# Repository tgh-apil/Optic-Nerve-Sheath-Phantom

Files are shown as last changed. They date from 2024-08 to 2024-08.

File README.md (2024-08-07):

# Optic-Nerve-Sheath-Phantom
A transorbital ultrasonographic optic nerve sheath training phantom based on a model designed by Dr. Zakir Hajat, Dr. Michael Dinsmore, and Dr. Lashmi Venkatraghavan.

This model is based on the pre-existing transorbital ultrasonographic optic nerve sheath phantom described in a [2020 paper by Hajat et al.](https://doi.org/10.1097/ana.0000000000000592), and was developed alongside Dr. Michael Dinsmore for the dual purposes of improving the realism of the training phantom by providing a human face-shaped case in which to house the inner components of the phantom (i.e. the eye and optic nerve sheath) and of increasing its longevity by replacing the gelatine and psyllium fiber with ballistics gel. It also replaces difficult to access components (namely the pediatric microcuffed endotracheal tube) with silicone components that are relatively easy to manufacture. This phantom is intended for training in the measurement of optic nerve sheath diameter through noninvasive ultrasonography.

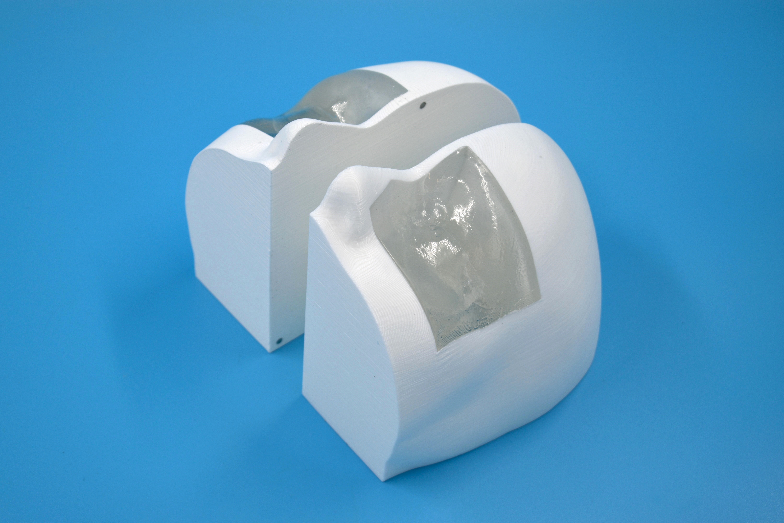
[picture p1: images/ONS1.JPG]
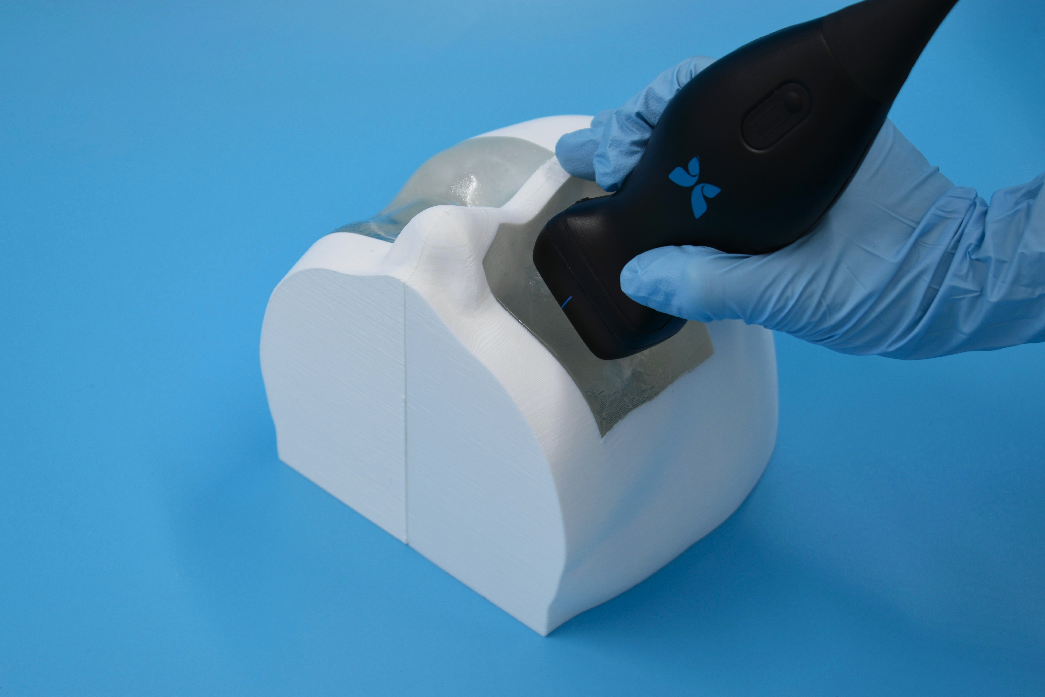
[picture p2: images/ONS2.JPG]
  

Note: The headform model was modified from NIOSH National Personal Protective Technology Laboratory (NPPTL)’s medium size ISO Digital Headform: https://www.cdc.gov/niosh/npptl/topics/respirators/headforms/default.html

This model was developed at the Lynn & Arnold Irwin Advanced Perioperative Imaging Lab, Toronto General Hospital, University Health Network.

## Parts, Materials & Equipment
### Printed Parts List
The files for these parts can be found in the [*/stl files/*](stl%20files) directory.

*/stl files/intermediate molds/* — for silicone casting of intermediate mold
* ONSl_intmold_1.stl
* ONSl_intmold_2.stl
* ONSr_intmold_1.stl
* ONSr_intmold_2.stl

*/stl files/sheath molds/* — for silicone casting of nerve sheath
* ONS_sheathmold_4_5mm_1.stl
* ONS_sheathmold_4_5mm_2.stl
* ONS_sheathmold_5_5mm_1.stl
* ONS_sheathmold_5_5mm_2.stl
* ONS_sheathmold_6_5mm_1.stl
* ONS_sheathmold_6_5mm_2.stl

*/stl files/case/* — for housing eye and nerve sheath in ballistics gel
* ONSl_case.stl
* ONSr_case.stl

*/stl files/other/* 
* ONS_ramp.stl

### Hardware
* 8 x M4 8mm screws
* Table tennis balls (40mm in diameter)
* Super glue
* Magnets (3mm OD), 6 per head (i.e. 3 per half head)

### Printing
* PLA (polylactic acid) filament
* Fused Deposition Modelling 3D printer

### Casting
* [Smooth-On’s Mold Star 20T Silicone Rubber](https://www.smooth-on.com/products/mold-star-20t/) (or another silicone of similar hardness) 
* Hot glue gun
* 5mL syringe
* [Clear Ballistics - 10% Ballistics Gel](https://www.clearballistics.com/product/10-ballistics-gel)
* [Humimic Medical - Medical Ballistics Gel #5](https://humimic.com/product/gelatin-5-medical-gel-by-the-pound/) 
* Slow cooker
* Heat gun

## Assembly Instructions
### Intermediate Mold Silicone Casting
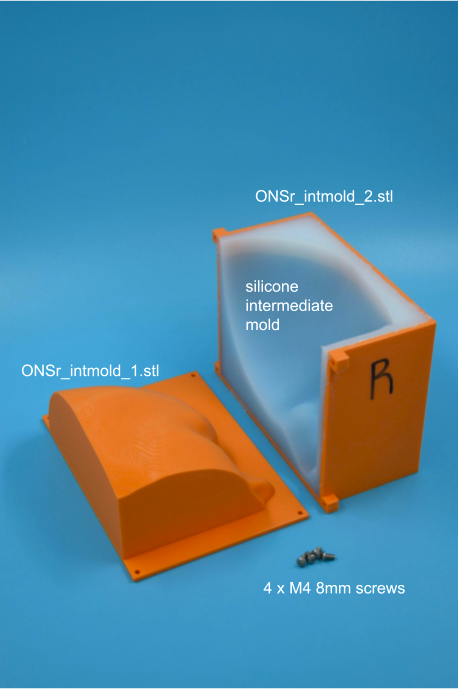
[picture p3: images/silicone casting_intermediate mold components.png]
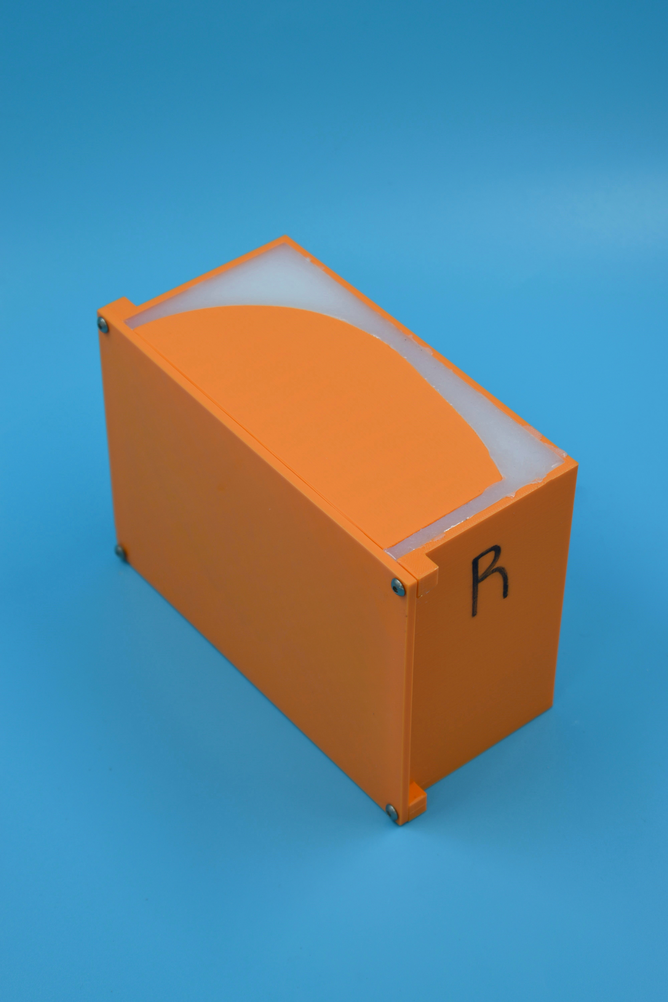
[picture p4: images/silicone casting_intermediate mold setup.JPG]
  

1. Print all components in */stl files/intermediate molds*.
2. Assemble parts 1 and 2 together using 4 x M4 12mm screws per side. Use a hot glue gun to seal the seams between the two components to ensure silicone does not leak out.
3. Mix a total of 1250mL of silicone according to manufacturer instructions.
   - Note: if working with a silicone with a short pot life (such as Mold Star 20T), degassing is not recommended.
4. Pour silicone into the assembled mold and allow to cure according to manufacturer instructions.
5. Once cured, disassemble the mold and remove part 1 of the mold (i.e. the face positive). Part 2 should remain attached to the silicone to provide structural support.
   - Note: there may be a small air bubble beside the eye portion of the mold, but this can be filled by applying a small additional amount of silicone into the cavity and placing it back into the mold to cure a second time.

### Eye and Nerve Sheath Silicone Casting
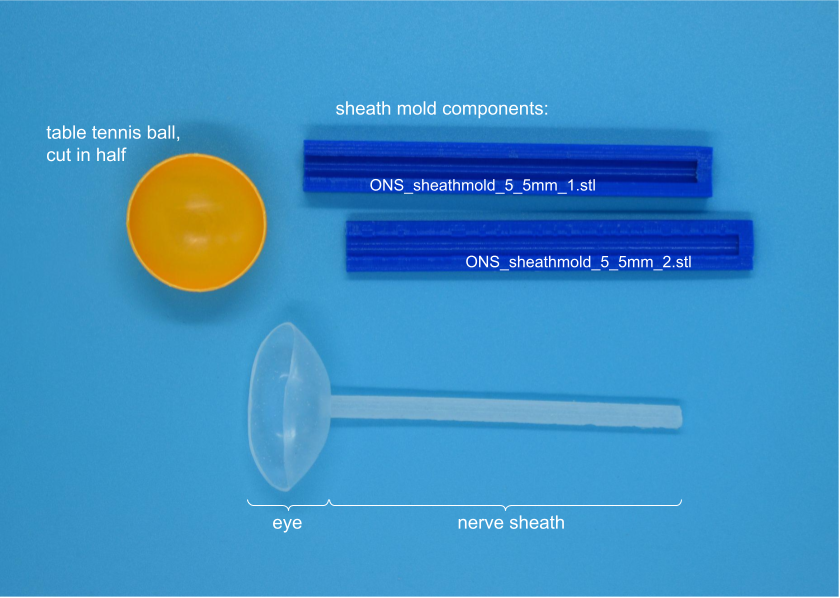
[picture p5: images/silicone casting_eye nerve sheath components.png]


*Nerve sheath*
1. Print the mold components in */stl files/sheath molds/* corresponding to the desired sheath diameter. Ex: a file with the 5_5mm suffix will correspond to a sheath diameter of 5.5mm.
   - Note: filing may be needed to ensure parts 1 and 2 fit together neatly.
2. Assemble parts 1 and 2 together using hot glue.
3. Mix a total of 5mL of silicone according to manufacturer instructions. A fast-drying silicone (such as Mold Star 20T) is recommended.
4. Inject into mold using syringe. 
   - Note: air bubbles may result in the finished product. Though these do not typically affect the ultrasound image, they can be removed by tipping the mold upside down, which causes the air bubbles to rise to the top. The amount of silicone injected is in excess of the volume of the mold, thus allowing for a long sheath to be produced even as some silicone leaks out of the upside down mold as it cures.
5. Allow silicone to cure according to manufacturer instructions. Once cured, remove hot glue and open mold. Trim the sides of the sheath and cut to length (roughly 10 cm is adequate), ensuring one end is as flat as possible for attaching to eye.

*Eye*
1. Cut a table tennis ball in half, creating two hemispheres.
2. Mix a total of 20mL of silicone according to manufacturer instructions. A fast-drying and sturdy silicone (such as Mold Star 20T) is recommended. It is also recommended to use the same silicone as for the sheath.
3. Pour into a table tennis ball hemisphere, ensuring all of the inside surface is coated with silicone.
4. Tip upside down and place on a broad grate or similar such that the silicone can pour out of the hemisphere.
5. Allow silicone to cure according to manufacturer instructions. Once cured, the silicone should have formed a thin, smooth skin in the shape of the inside of the table tennis ball. Remove carefully and trim any excess dripping off the sides.

*Connecting the two*
1. Clamp or hang the nerve sheath in place above the upturned “eye” such that the end of the sheath touches the top of the “eye”. 
   - Note: placing the eye on top of a table tennis ball hemisphere or another 4 cm diameter ball will help it to retain its shape, making the connection process easier.
2. Mix a small amount of silicone according to manufacturer instructions (2mL total is adequate). It is recommended to use the same silicone as for the sheath and eye.
3. Carefully dab silicone onto the end of the sheath, then place it on top of the eye and smooth out any excess silicone around the point of connection.
4. Allow silicone to cure according to manufacturer instructions. Once cured, the two components should be connected into one.

## Ballistics Gel Casting & Head Assembly
**CAUTION:** Use appropriate heat-proof gloves when working with liquefied ballistic gel and/or heat gun.<br>**CAUTION:** work only in a very well ventilated area. A fume hood is highly recommended.

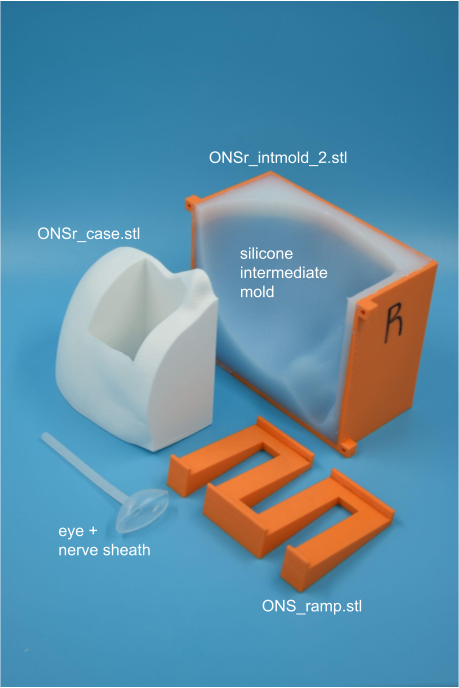
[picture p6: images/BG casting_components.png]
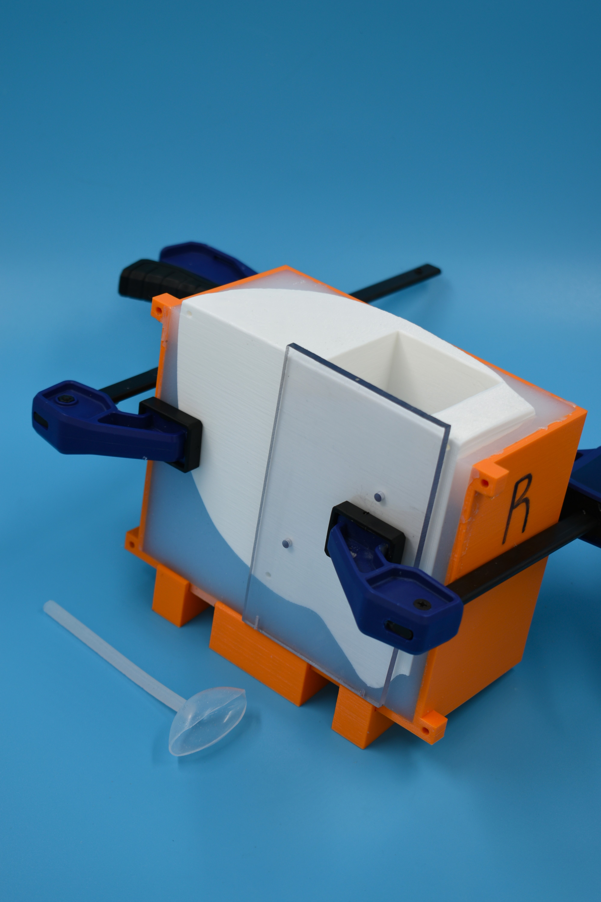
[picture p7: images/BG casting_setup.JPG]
  

1. Melt at least 125 g 10% gel and 125 g Humimic #5 gel (a total of 250 g) in a slow cooker at 105C - 115C (approx. 225F - 240F).
2. Print the case components (*/stl files/case/*) as well as the tilting ramp (*/stl files/other/*).
3. Place the case into the corresponding intermediate silicone mold so that the outside of the case is flush with the silicone. Clamp into position. 
   - Note: in order to prevent deformation of the case under high temperatures, it may be helpful to place a thin plastic or wood plate between the case and the clamp, covering the thinnest wall of the case.
4. Place the case and mold onto the tilting ramp so that the flat side of the case is slightly elevated. This will help ensure the eye and nerve sheath are properly oriented.
5. Pour ballistics gel into the case until the silicone in the window is just covered and allow to cool.
6. Place the eye-nerve sheath into something that will allow the eye to hold its shape (for example, a ping pong ball hemisphere with a hole large enough to accommodate the sheath). Pour ballistics gel into the eye until full and allow to cool. Once cool remove the eye-nerve sheath and trim any excess silicone around the top so that the gel is slightly concave. This will help prevent air bubbles when placing the eye into the case.
7. Use a heat gun to gently melt the surface of the gel in both the case and the eye, then place the eye into the case. See the figure below for approximate placement. The melted surfaces allow for a few seconds of mobility during which it is possible to correct the position of the eye and to compress out any air bubbles. Position the nerve sheath so that it is straight and vertical.
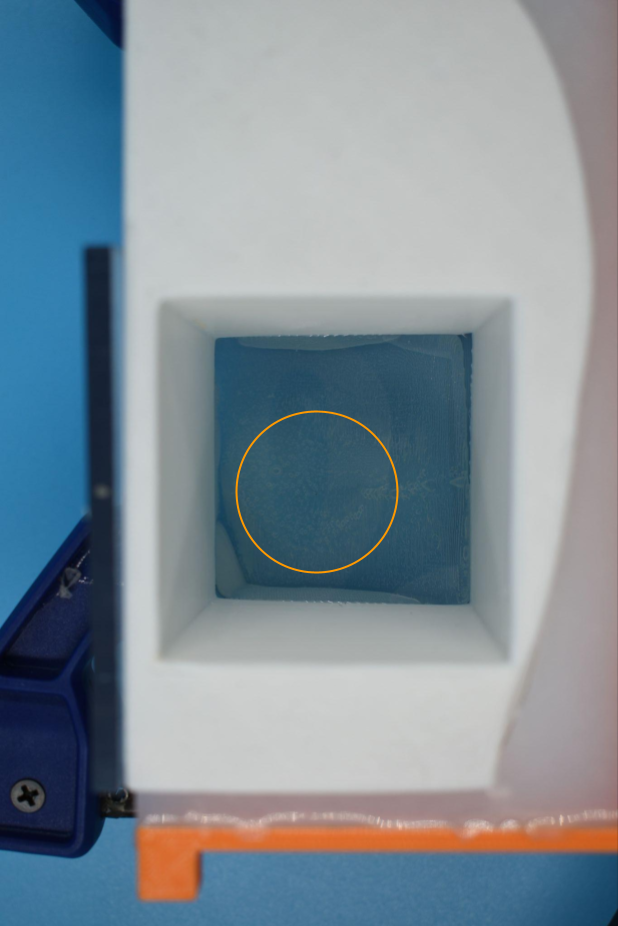
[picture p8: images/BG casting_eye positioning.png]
   - 
   - Note: the presence of air bubbles does not necessarily render the phantom unusable so long as they are not in the centre of the eye where they will block the nerve sheath during ultrasound. If this occurs, remove the eye-nerve sheath and its gel, and repeat steps 6 and 7.
8. Once cooled, pour enough ballistics gel into the case to cover the nerve sheath to a depth of roughly 5 centimetres. Allow to cool again.
9. Once cooled, unclamp and remove the case from the mold. Trim the nerve sheath so that it does not stick out beyond the case. Use a heat gun to gently heat the surface of the ballistics gel in the case to smooth out the texture imparted to it by the silicone mold.

## Final Assembly
1. Use a ⅛-inch drill bit to tap the pre-printed magnet holes in the case.
2. Apply a small amount of super glue into a hole and insert a 3mm magnet. Do the same for all holes, taking care to ensure the opposing magnets in each case half do not repel one another.

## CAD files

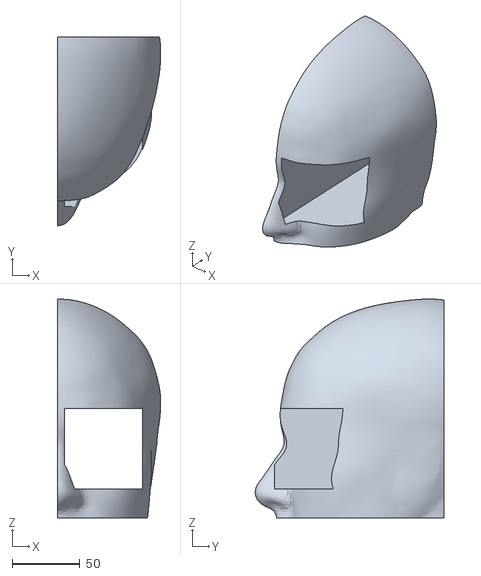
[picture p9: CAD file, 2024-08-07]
stl files/case/ONSl_case.stl
76.2 x 139.1 x 161.4

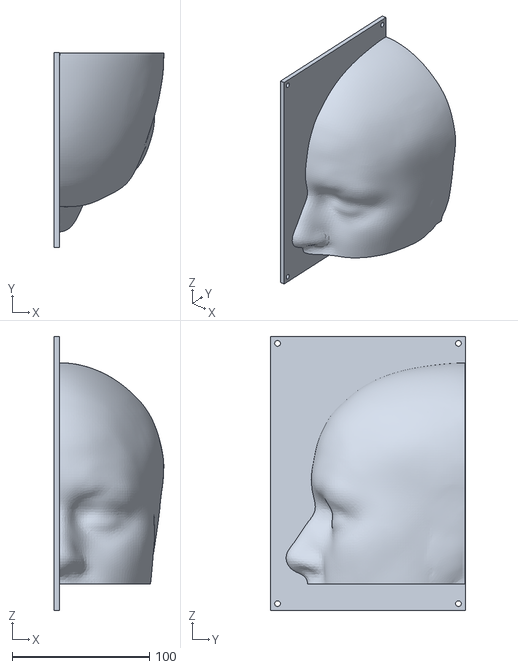
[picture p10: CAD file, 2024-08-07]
stl files/intermediate molds/ONSl_intmold_1.stl
80.0 x 142.0 x 200.0

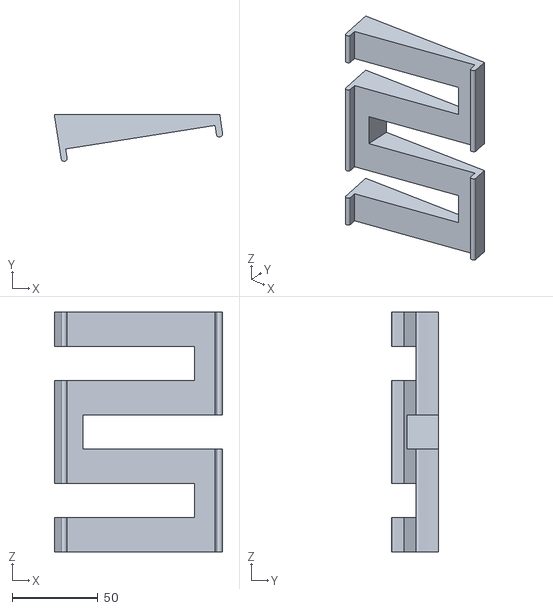
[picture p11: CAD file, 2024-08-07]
stl files/other/ONS_ramp.stl
98.3 x 27.2 x 140.0

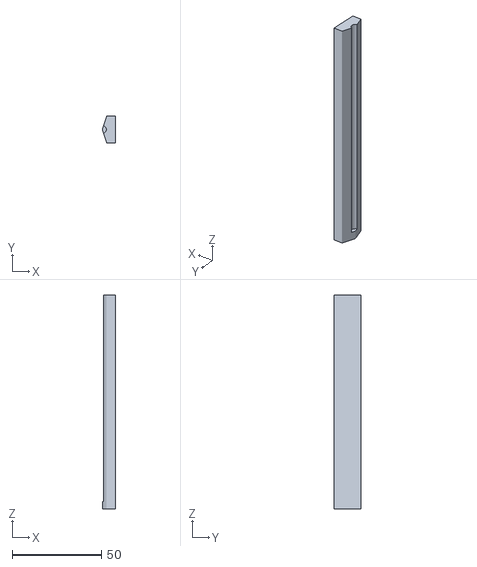
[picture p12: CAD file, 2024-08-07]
stl files/sheath molds/ONS_sheathmold_4_5mm_2.stl
7.50 x 15.0 x 120.0

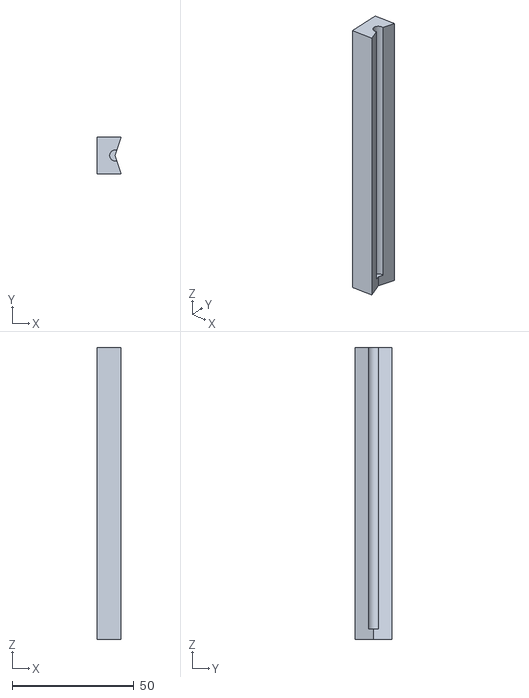
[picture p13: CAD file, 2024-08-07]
stl files/sheath molds/ONS_sheathmold_4_5mm_1.stl
9.95 x 15.0 x 120.0

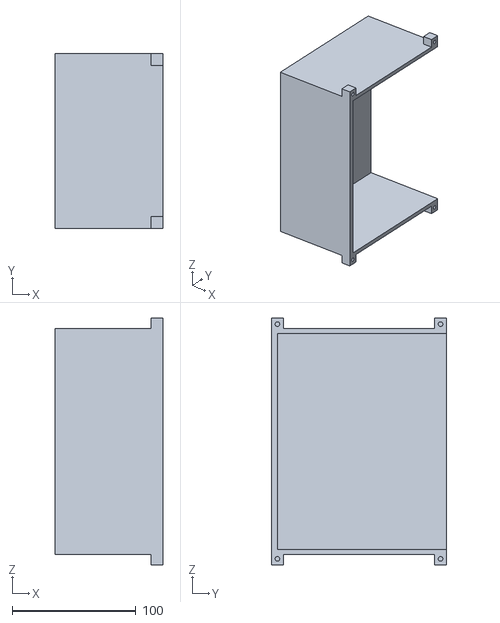
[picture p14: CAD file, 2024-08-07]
stl files/intermediate molds/ONSr_intmold_2.stl
87.7 x 142.0 x 199.9

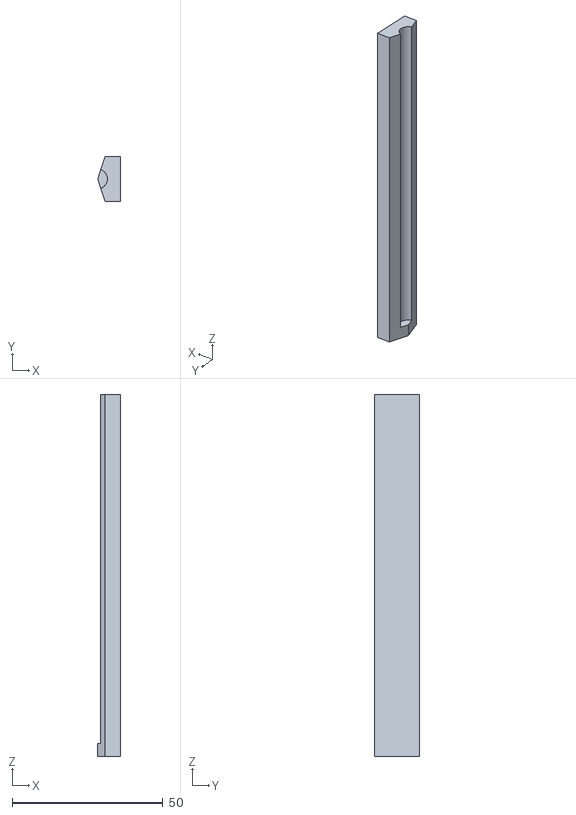
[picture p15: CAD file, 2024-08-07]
stl files/sheath molds/ONS_sheathmold_6_5mm_2.stl
7.50 x 15.0 x 120.0

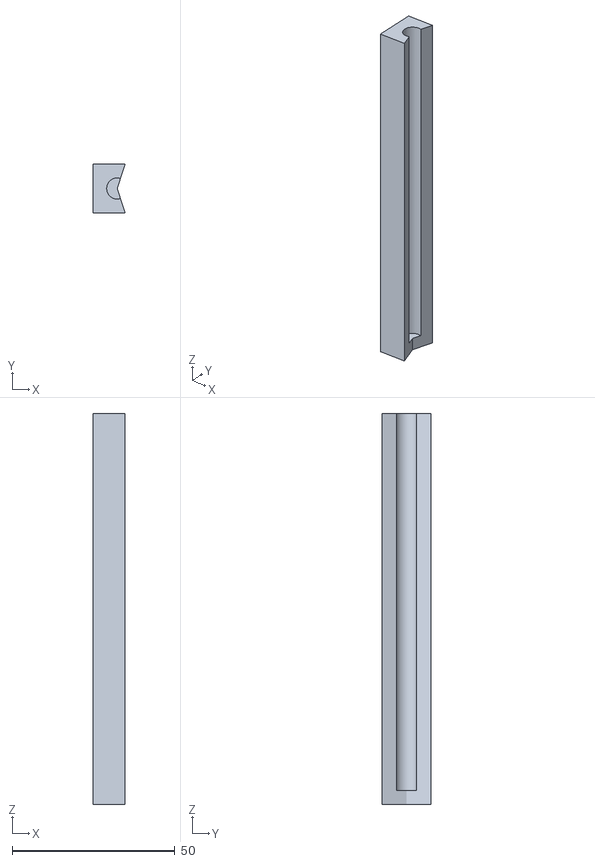
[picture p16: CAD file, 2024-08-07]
stl files/sheath molds/ONS_sheathmold_6_5mm_1.stl
9.95 x 15.0 x 120.0

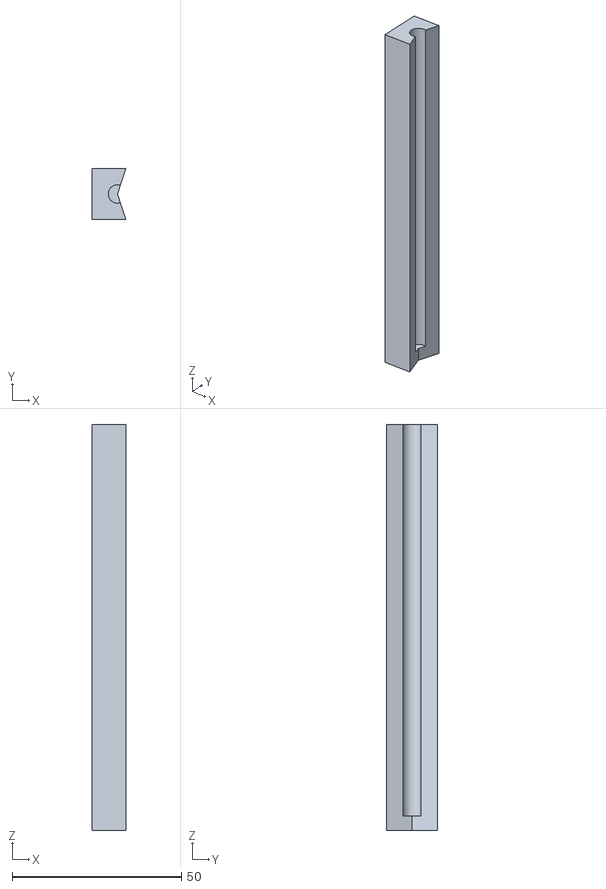
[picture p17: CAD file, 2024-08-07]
stl files/sheath molds/ONS_sheathmold_5_5mm_1.stl
9.95 x 15.0 x 120.0

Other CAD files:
stl files/case/ONSr_case.stl
stl files/intermediate molds/ONSr_intmold_1.stl
stl files/intermediate molds/ONSl_intmold_2.stl
stl files/sheath molds/ONS_sheathmold_5_5mm_2.stl

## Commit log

2024-08-07 Delete CAD Files directory
    to be replaced with updated stl files
    [left bottom.3mf, left bottom.stl, left lid.stl, left mold 1.stl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]
2024-08-07 adding updated stl files
    [ONS_ramp.stl, ONS_sheathmold_4_5mm_1.stl, ONS_sheathmold_4_5mm_2.stl, ONS_sheathmold_5_5mm_1.stl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]
